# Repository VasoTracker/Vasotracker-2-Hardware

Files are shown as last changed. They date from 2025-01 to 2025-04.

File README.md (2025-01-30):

# VasoTracker 2.0

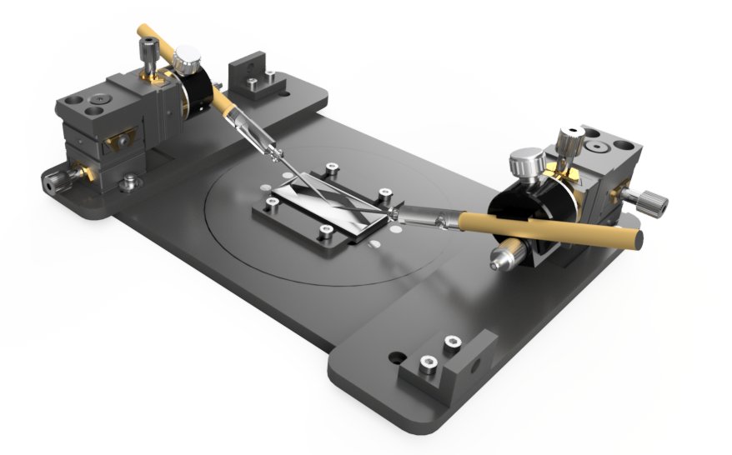
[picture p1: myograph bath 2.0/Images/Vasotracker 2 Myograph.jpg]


**VasoTracker 2.0** is a cost-effective, open-source system designed for measuring and tracking the diameter of isolated, pressurized blood vessels. As an accessible alternative to commercial pressure myograph systems, it costs approximately £13,500—about 25% of the price of typical commercial options.

Whether you’re new to vascular research or looking to optimize your lab's setup, VasoTracker 2.0 offers a modular and customizable solution for assessing blood vessel function.

For full details: see https://vasotracker.com/

## Table of Contents

- [Publications](#publications)
- [Core VasoTracker Components](#core-vasotracker-components)
- [Additional Components for a Complete System](#additional-components-for-a-complete-system)
- [Contributors for VasoTracker 2.0](#contributors-for-vasotracker-20)

## Publications

- VasoTracker 2.0 will soon be published as a preprint.
- The original VasoTracker 1.0 system is described here: DOI: [10.3389/fphys.2019.00099](https://www.frontiersin.org/articles/10.3389/fphys.2019.00099/full).
- [Click here to see a list of papers citing the first VasoTracker version](https://scholar.google.com/scholar?cites=12876987194916375307&as_sdt=2005&sciodt=0,5&hl=en).

## Core VasoTracker Components

**Approximate Build Cost: £3,320**

- **Bath Chamber (~£2,500)**  
  [Pressure Myograph](https://github.com/VasoTracker/VasoTracker-2/tree/main/myograph%20bath%202.0)
  
- **Temperature & Pressure Monitor (~£320)**  
  [Temperature & Pressure Sensor](https://github.com/VasoTracker/VasoTracker-2/tree/main/temperature%20%26%20pressure%20monitor)
  
- **VasoMoto Pressure Control System (~£500)**  
  [VasoMoto System](https://github.com/DrN8PhD/VasoMoto)
  
- **VasoTracker Software (Free)**  
  [VasoTracker Software](https://github.com/VasoTracker/VasoTracker-2/tree/main/vasotracker%202.0)

For details, refer to the [**VasoTracker 2.0 System Guide**](https://github.com/VasoTracker/VasoTracker-2/blob/main/VasoTracker%202%20System%20Guide.pdf).

## Additional Components for a Complete System

**Approximate Cost for New Components: £10,150**

To fully set up a VasoTracker-based pressure myography system, the following components are also required:

- **Microscope (inverted preferred) ~£5,000**
- **Camera (compatible with microscope) ~£400**
- **Laptop Computer (for data capture and analysis) ~£500**
- **Temperature Control System ~£4,250**

## Contributors for VasoTracker 2.0

**University of Strathclyde:**
- Calum Wilson
- Matthew D Lee
- John G McCarron
- Xun Zhang
- Charlotte Buckley

**University of Glasgow:**
- Christopher Osborne

**University of Vermont:**
- Osama Harraz

**Michigan State University:**
- Nathan R Tykocki

## License

Distributed under the terms of the [BSD-3-Clause] license,

VasoTracker is free and open source software/hardware.

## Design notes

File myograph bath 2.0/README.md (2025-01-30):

# VasoTracker 2.0 Pressure Myograph Chamber



The **VasoTracker 2.0 Pressure Myograph Chamber** is a multi-purpose design, and is ideal for experiments requiring blood vessel diameter measurement. The chamber was designed to sit on a standard microscope stage, but the baseplate was designed for compatibility with [Thorlabs motorized scanning stages](https://www.thorlabs.com/newgrouppage9.cfm?objectgroup_id=5360). Angled cannula holders allow vessels to be positioned near the coverglass at the bottom of the chamber for inverted confocal use, and also provide enough clearance to enable confocal imaging with large-diameter CFI60 on upright microscopes. 

We recommend that the custom parts are manufactured in POM-C material by commercial manufacturers (costs will scale with the number of baths ordered). 

## Table of Contents
- [Key Features](#key-Features)
- [Build & Operation Guide](#build--operation-guide)
- [Cost-Saving Tip](#cost-saving-tip)

## Key Features

- **Low-Volume Chamber:** The vessel chamber insert is designed for efficient use of reagents and environmental control, with only ~2 ml of volume.
- **Precision Positioning:** Independent XYZ positioning of both cannulas is enabled by dual pipette holders mounted on miniaturized 3-axis translation stages, ensuring accurate and flexible manipulation of vessels.
- **Precise Vessel Positioning:** The angled cannula design allows for easy vessel positioning near the coverslip, supporting low-working distance objectives on inverted microscopes, as well as water-dipping objectives on upright systems.
- **Durable Materials:** The base can be machined from POM-C, and the chamber insert from acrylic, making it durable and adaptable to various experimental conditions.
- **Magnetic Attachments:** Superfusion plumbing is attached securely with flexible magnetic holders, making it easy to manage and adjust.

## Build & Operation Guide

The monitor is constructed using readily available Arduino components. At the time of release, the total cost of the components is approximately **£315.66**, with pressure transducers accounting for a significant portion of the expense.

For a detailed list of components, step-by-step build instructions, and operational guidelines, please refer to the [**Bath Chamber User Manual**](https://github.com/VasoTracker/VasoTracker-2/blob/main/myograph%20bath%202.0/VasoTracker%202%20Bath%20Chamber%20Manual.pdf).

## Cost-Saving Tip

We recommend that the VasoTracker 2.0 Pressure Myograph  is machined out of POM-C (use acryllic for the actual chamber). Commercial CNC-machining costs scale with quantity - the price per unit drastically decreases when you order more than one of each part.

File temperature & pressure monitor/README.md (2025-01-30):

# VasoTracker Temperature & Pressure Monitor

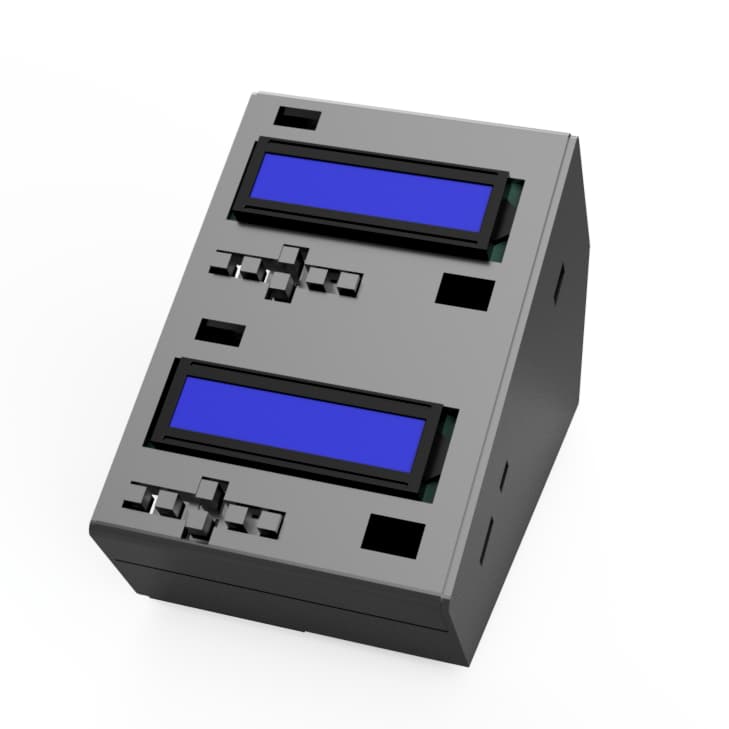
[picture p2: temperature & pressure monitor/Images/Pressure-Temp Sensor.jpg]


The **VasoTracker Temperature & Pressure Monitor** is an Arduino-based system designed for use with the VasoTracker myograph or any other setup that requires precise temperature and pressure monitoring. This modular device is easy to assemble and provides real-time data acquisition for experiments.

## Table of Contents
- [Key Features](#key-features-of-vasotracker-20)
- [Build & Operation Guide](#build--operation-guide)
- [Cost-Saving Tip](#cost-saving-tip)

## Key Features

- **Temperature Monitoring:** Accurately reads and displays temperature using a 10k NTC thermistor.
- **Pressure Monitoring:** Reads and displays pressure using flow-through pressure transducers.
- **Data Integration:** Streams data to the VasoTracker 2.0 GUI via the serial port for real-time acquisition and display.

## Build & Operation Guide

The monitor is constructed using readily available Arduino components. At the time of release, the total cost of the components is approximately **£315.66**, with pressure transducers accounting for a significant portion of the expense.

For a detailed list of components, step-by-step build instructions, and operational guidelines, please refer to the [**Temperature & Pressure Monitor User Manual**](https://github.com/VasoTracker/VasoTracker-2/blob/main/temperature%20%26%20pressure%20monitor/VasoTracker%202%20Temperature%20%26%20Pressure%20Monitor%20Manual.pdf).

## Cost-Saving Tip

You can significantly reduce the cost by opting for **disposable inline pressure transducers**, which are available for as low as **£10 each**. This is the approach used by VasoMoto to cut costs.

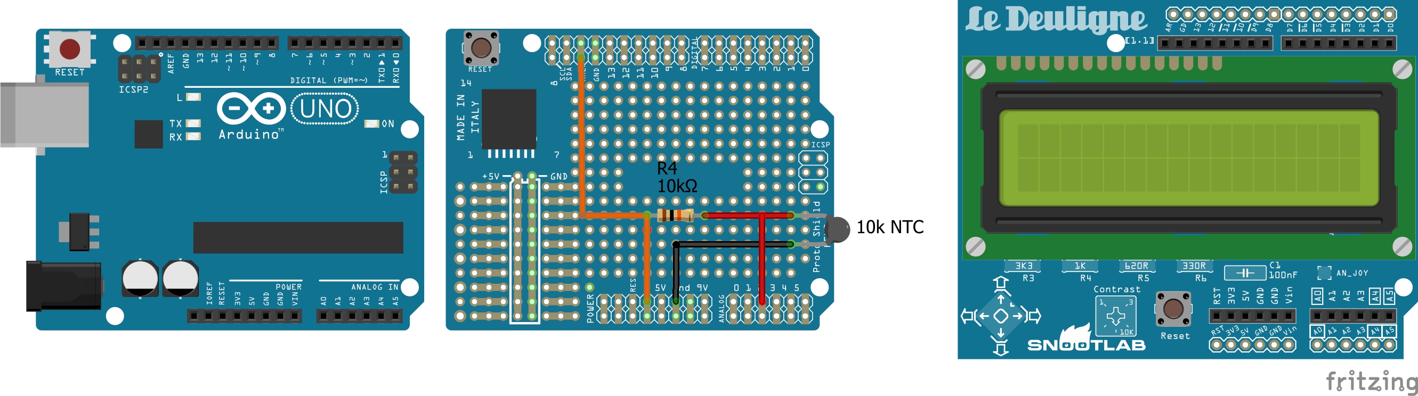
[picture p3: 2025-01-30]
temperature & pressure monitor/Images/Arduino Temp Sensor.jpg

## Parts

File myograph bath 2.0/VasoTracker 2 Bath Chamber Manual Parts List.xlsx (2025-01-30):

VasoTracker Pressure Myograph Chamber Parts
CNC Machined Components
Component | Supplier | Product # | Qty | Price | Total | Supplier Link
01_Nikon_Baseplate** | VasoTracker | - | 1 | £250.00 | £250.00 | VasoTracker GitHub (https://github.com/VasoTracker/VasoTracker-2/tree/main)
02_Chamber_Base** | VasoTracker | - | 1 | £130.00 | £130.00 | VasoTracker GitHub (https://github.com/VasoTracker/VasoTracker-2/tree/main)
03_Chamber_low_volume** | VasoTracker | - | 1 | £140.00 | £140.00 | VasoTracker GitHub (https://github.com/VasoTracker/VasoTracker-2/tree/main)
04_Clamp** | VasoTracker | - | 2 | £97.00 | £194.00 | VasoTracker GitHub (https://github.com/VasoTracker/VasoTracker-2/tree/main)
05_Tubing Connector** | VasoTracker | - | 2 | £99.00 | £198.00 | VasoTracker GitHub (https://github.com/VasoTracker/VasoTracker-2/tree/main)
**Prices scale with quantity!
Prices correct 10/2024 |  | Total |  |  | £912.00
3D Printed Components
Component | Supplier | Product # | Qty | Price | Total | Supplier Link
Magnetic Plumbing Holder | VasoTracker | - | 2 | £1.00 | £2.00 | VasoTracker GitHub (https://github.com/VasoTracker/VasoTracker-2/tree/main)
Prices correct 10/2024 |  | Total |  |  | £2.00
Commercial Components
Component | Supplier | Product # | Qty | Price | Total | Supplier Link
Micromanipulators | Thorlabs | DT12XYZ/M | 2 | £288.00 | £576.00 | Thorlabs (https://www.thorlabs.com/thorproduct.cfm?partnumber=DT12XYZ/m)
Rotatable cannula clamps | Siskiyou | MXC | 2 | £105.35 | £210.70 | Siskiyou (https://siskiyou.com/mxc/)
1.5 mm glass cannula holders | WPI Inc | MPH3 | 2 | £64.00 | £128.00 | WPI Inc (https://www.wpiinc.com/var-3819-microelectrode-holder-mph3.html)
Handle for cannula holder | WPI Inc | 2505 | 2 | £31.00 | £62.00 | WPI Inc (https://www.wpiinc.com/2505-electrode-handle-63-mm.html)
Perfusion plumbing (bend needles) | Needlez | NB16G1.5B90 | 2 | £0.68 | £1.36 | Needlez (https://www.needlez.co.uk/product/16g-blunt-needle-1-5inch-38mm-bent-tip-90-deg/)
Prices correct 10/2024 |  | Total |  |  | £978.06
Consumables & Miscellaneous Supplies
Component | Supplier | Product # | Qty | Price | Total | Supplier Link
Coverglass (50 mm by 24 mm) | MarienFeld | MARI0102222 | 1 | £107.00 | £107.00 | VWR (https://uk.vwr.com/store/product/7803457/cover-glasses-for-fluorescence)
50x Magnets | Amazon | 5 mm diameter, 1 mm thick | 1 | £5.59 | £5.59 | Amazon (https://www.amazon.co.uk/100PCS-Magnets-Neodymium-Whiteboards-Picture/dp/B09H2W3TQZ)
50x Magnets | Amazon | 5 mm diameter, 2 mm thick | 1 | £3.99 | £3.99 | Amazon (https://www.amazon.co.uk/FINDMAG-Neodymium-Magnets-Whiteboard-Hobbies/dp/B0C81GTN8P)
Superglue | Amazon | Gorilla Glue | 1 | £3.37 | £3.37 | Amazon (https://www.amazon.co.uk/Gorilla-Superglue-3g-Pack-2/dp/B001C5I4BO/)
M3 Socket Screws | Amazon | NB16G1.5B90 | 1 | £10.99 | £10.99 | Amazon (https://www.amazon.co.uk/gp/product/B09J2MNSMZ/)
M4 Socket Screws | Amazon | MARI0102222 | 1 | £10.99 | £10.99 | Amazon (https://www.amazon.co.uk/gp/product/B0CP1R19N5/)
Prices correct 10/2024 |  | Total |  |  | £141.93
Tubing & Connectors
Component | Supplier | Product # | Qty | Price | Total | Supplier Link
Masterflex 1.22 ID tubing (100 ft roll) | VWR | MFLX06449-31 | 1 | £201.00 | £201.00 | VWR (https://uk.vwr.com/store/item/EU7157222/masterflex-ismatec-microbore-pump-tubing-tygon-s3tm-e-lfl-avantor)
Masterflex 1.52 ID tubing (100 ft roll) | VWR | MFLX06460-36 | 1 | £157.00 | £157.00 | VWR (https://uk.vwr.com/store/item/EU7098238/masterflex-ismatec-microbore-pump-tubing-tygon-e-lab-avantor)
Female luer (1/16" barb; pack of 25) | VWR | GY-45502-00 | 1 | £28.90 | £28.90 | VWR (https://uk.vwr.com/store/item/EU7104706/masterflex-adapter-fittings-female-luer-to-hose-barb-bulkhead-polypropylene-avantor)
Male luer (1/16" barb; pack of 25) | VWR | MFLX45504-00 | 1 | £20.40 | £20.40 | VWR (https://uk.vwr.com/store/item/EU7104664/masterflex-adapter-fittings-male-luer-to-hose-barb-straight-polycarbonate-avantor)
Luer stopcock (pack of 10) | VWR | MFLX30600-02 | 1 | £34.60 | £34.60 | VWR (https://uk.vwr.com/store/item/EU7103411/masterflex-luer-stopcock-fittings-polycarbonate-avantor)
Threaded Luer (pack of 25) | VWR | MFLX45508-30 | 1 | £28.90 | £28.90 | VWR (https://uk.vwr.com/store/item/EU7104706/masterflex-adapter-fittings-female-luer-to-hose-barb-bulkhead-polypropylene-avantor)
Prices correct 10/2024 |  | Total |  |  | £470.80
Total Price |  |  |  |  | £2504.79

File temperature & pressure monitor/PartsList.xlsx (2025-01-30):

VasoTracker Temperature & Pressure Monitor Parts
3D Printed Parts
3D Printed Enclosure | VasoTracker | - | 1 | £0 | £0 | GitHub (https://github.com/VasoTracker/VasoTracker-2)
Prices correct 10/2024 |  | Total |  |  | £0.00
VasoTracker Temperature Monitor
Component | Supplier | Product # | Qty | Price | Total | Supplier Link
Arduino Uno** | Arduino | RB-Ard-34 | 1 | £26.50 | £26.50 | RobotShop (https://uk.robotshop.com/products/arduino-uno-r3-usb-microcontroller)
12V power supply | RS | 903-7048 | 1 | £8.33 | £8.33 | RS (https://uk.rs-online.com/web/p/ac-dc-adapters/1753303)
Arduino Proto Shield | Skinflint | A000077 | 1 | £13.50 | £13.50 | SkinFlint (https://skinflint.co.uk/arduino-proto-shield-uno-a000077-a799462.html)
LCD Shield | RobotShop | RB-Cyt-73 | 1 | £3.64 | £3.64 | RobotShop (https://uk.robotshop.com/products/cytron-lcd-keypad-shield-arduino)
10k NTC Thermistor | Adafruit | 372 | 1 | £3.06 | £3.06 | DigiKey (https://www.digikey.co.uk/en/products/detail/adafruit-industries-llc/372/6051772)
Resistor kit | RobotShop | RES-E12 | 1 | £13.80 | £13.80 | RobotShop (https://uk.robotshop.com/products/resistor-kit-610pk)
Jumper wire kit | RobotShop | RB-Cix-02 | 1 | £3.77 | £3.77 | RobotShop (https://uk.robotshop.com/products/140-piece-pre-formed-jumper-wire-kit)
2-pin Screw Terminal | RobotShop | RB-Dfr-465 | 1 | £0.76 | £0.76 | RobotShop (https://uk.robotshop.com/products/2-pin-screw-terminal-35mm)
Prices correct 10/2024 |  | Total |  |  | £73.36
VasoTracker Pressure Monitor
Component | Supplier | Product # | Qty | Price | Total | Supplier Link
Arduino Uno** | Arduino | RB-Ard-34 | 1 | £26.50 | £26.50 | RobotShop (https://uk.robotshop.com/products/arduino-uno-r3-usb-microcontroller)
12V power supply | RS | 903-7048 | 1 | £8.33 | £8.33 | RS (https://uk.rs-online.com/web/p/ac-dc-adapters/1753303)
Wheatstone bridge amplifier shield | RobotShop | RB-Onl-38 | 1 | £45.63 | £45.63 | RobotShop (https://www.robotshop.com/uk/strain-gauge-load-cell-amplifier-shield-2ch.html)
LCD Shield | RobotShop | RB-Cyt-73 | 1 | £3.64 | £3.64 | RobotShop (https://uk.robotshop.com/products/cytron-lcd-keypad-shield-arduino)
Inline pressure transducers | Honeywell | 26PCDFG5G | 2 | £74.55 | £149.10 | Mouser (https://www.mouser.co.uk/ProductDetail/Honeywell/26PCDFG5G/)
12” 4-pin jumper wire | RobotShop | RB-Spa-1107 | 2 | £0.60 | £1.20 | RobotShop (https://uk.robotshop.com/products/12-4-pin-jumper-wire)
Arduino stackable headers | RobotShop | RB-Spa-928 | 1 | £1.67 | £1.67 | RobotShop (https://uk.robotshop.com/products/arduino-r3-stackable-headers)
Female to female jumper | RobotShop | RB-Gog-65 | 1 | £4.31 | £4.31 | RobotShop (https://uk.robotshop.com/products/assorted-silicon-wire-jumper-22-awg-65pk-f-f)
Heatshrink tubing | RobotShop | RB-Gog-47 | 1 | £1.92 | £1.92 | RobotShop (https://uk.robotshop.com/products/shrink-tube-variety-pack)
Prices correct 10/2024 |  | Total |  |  | £242.30
Total Price |  |  |  |  | £315.66

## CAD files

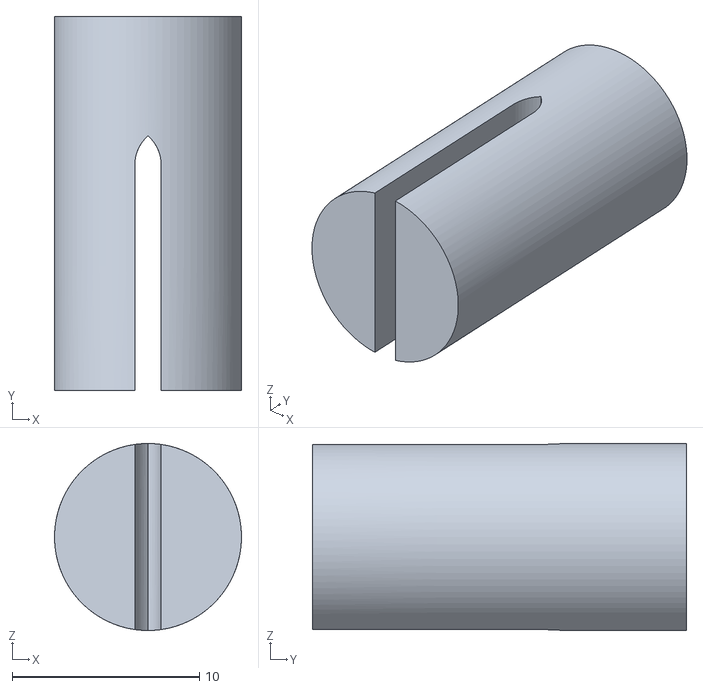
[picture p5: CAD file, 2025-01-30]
myograph bath 2.0/3D Print Files/plumbing_holder_large v1.stl
10.0 x 20.0 x 10.0

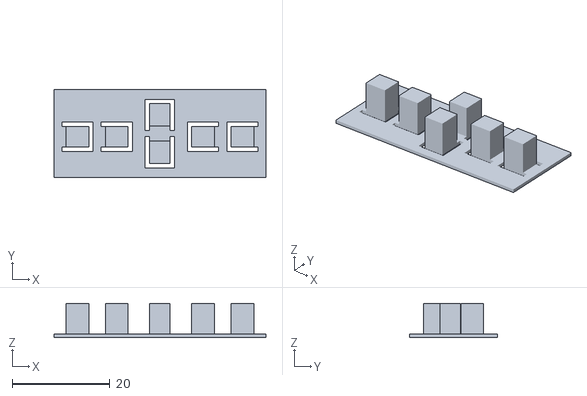
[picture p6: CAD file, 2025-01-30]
temperature & pressure monitor/3D Printed Enclosures/CombiBox/buttons.stl
43.3 x 18.0 x 7.02

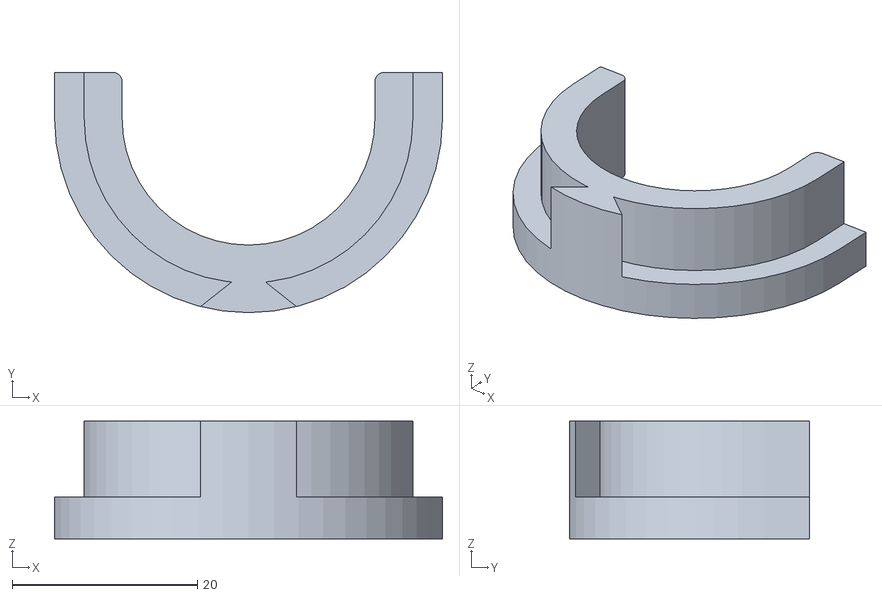
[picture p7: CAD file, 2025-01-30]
temperature & pressure monitor/3D Printed Enclosures/VasoMoto/VasoMoto Printed Parts/VasoMoto-tubing-spacer-2.stl
41.9 x 26.0 x 12.7

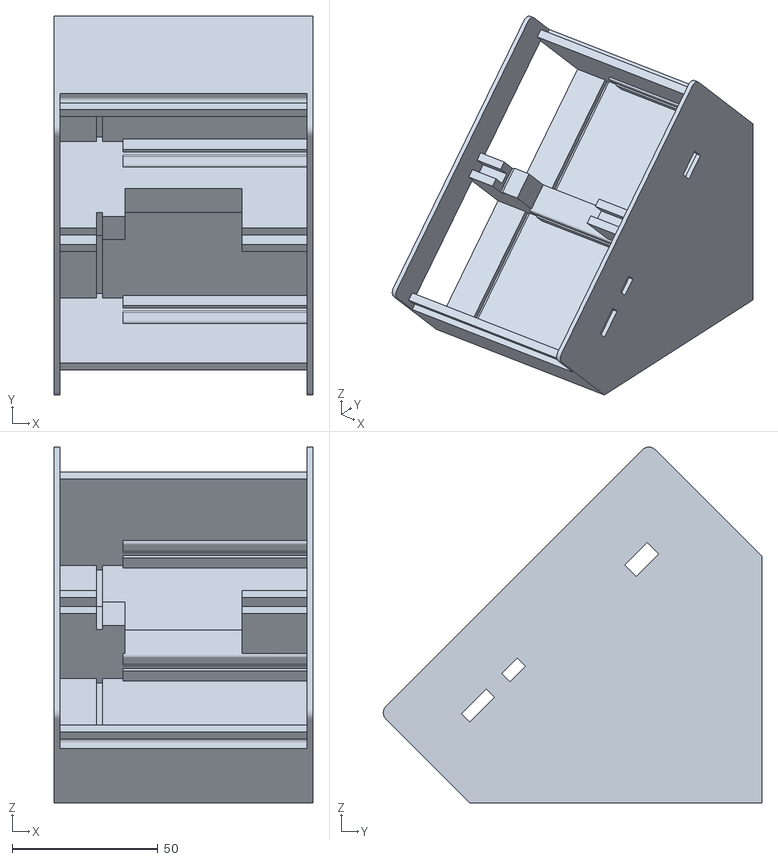
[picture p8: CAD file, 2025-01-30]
temperature & pressure monitor/3D Printed Enclosures/CombiBox/Arduino V7 combibox base.stl
88.6 x 129.8 x 122.0

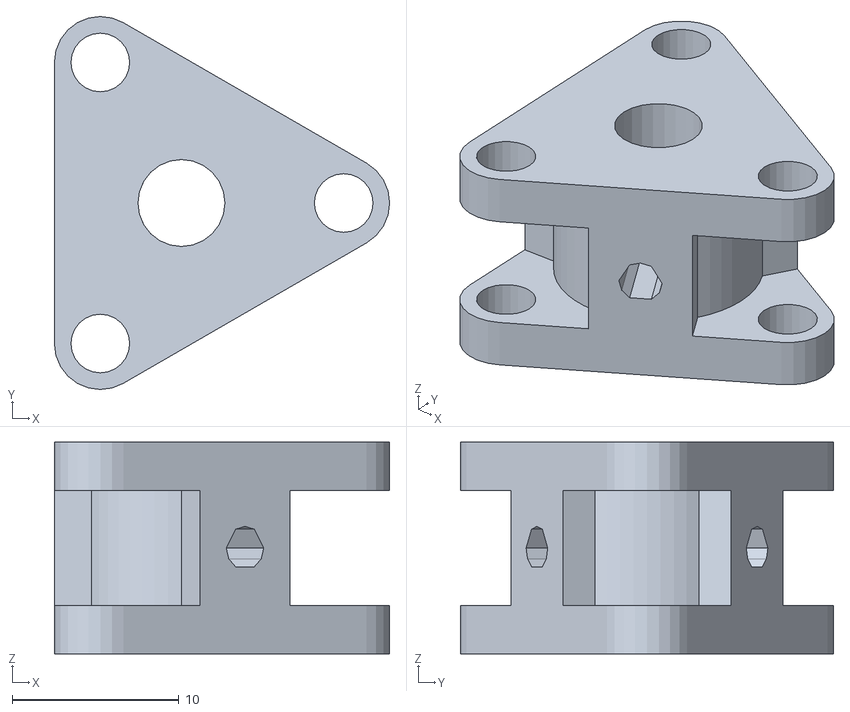
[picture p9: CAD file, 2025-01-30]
temperature & pressure monitor/3D Printed Enclosures/VasoMoto/VasoMoto Printed Parts/VasoMoto-pumphead.stl
20.1 x 22.4 x 12.7

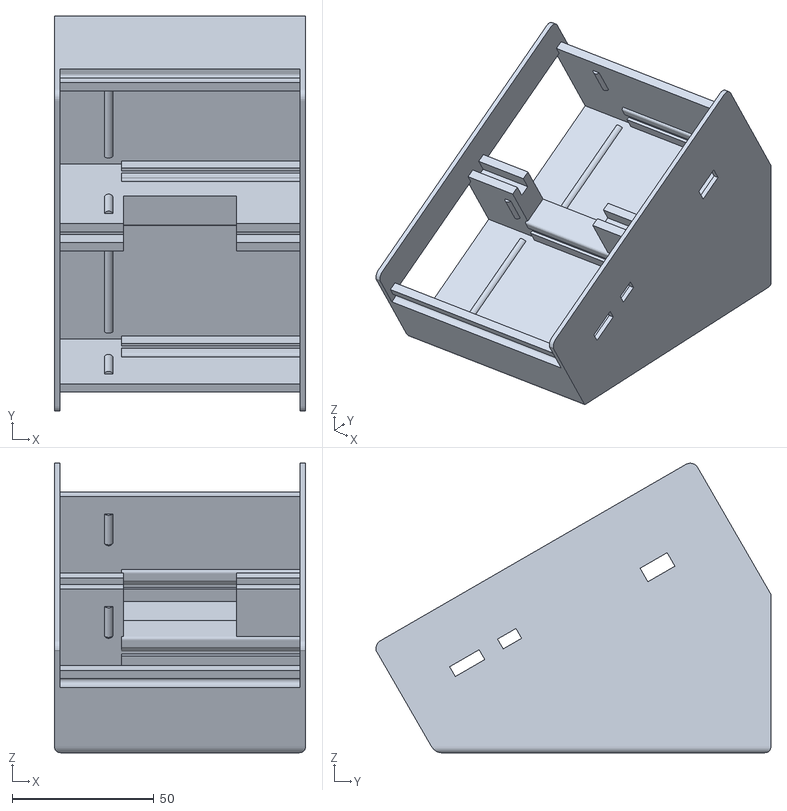
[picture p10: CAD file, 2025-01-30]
temperature & pressure monitor/3D Printed Enclosures/CombiBox/Arduino V7 combibox base 2.stl
88.6 x 139.3 x 102.2

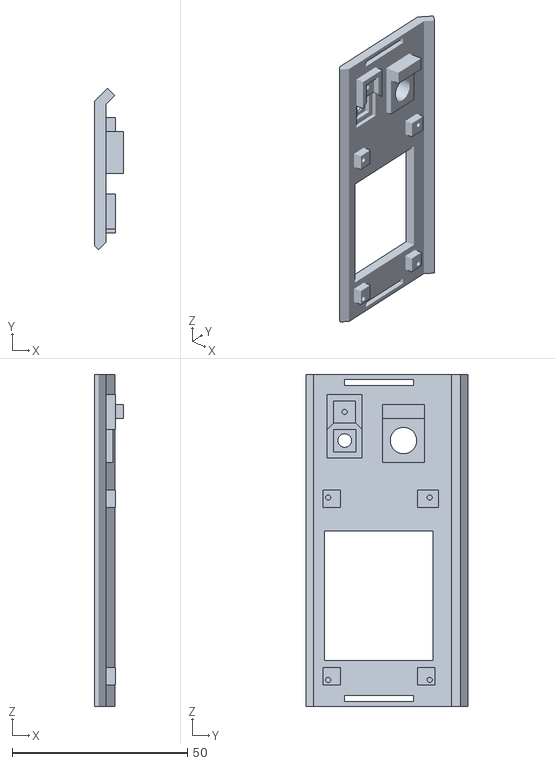
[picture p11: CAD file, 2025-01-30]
temperature & pressure monitor/3D Printed Enclosures/VasoMoto/VasoMoto Printed Parts/VasoMoto-LCD-button.stl
8.29 x 46.2 x 94.8

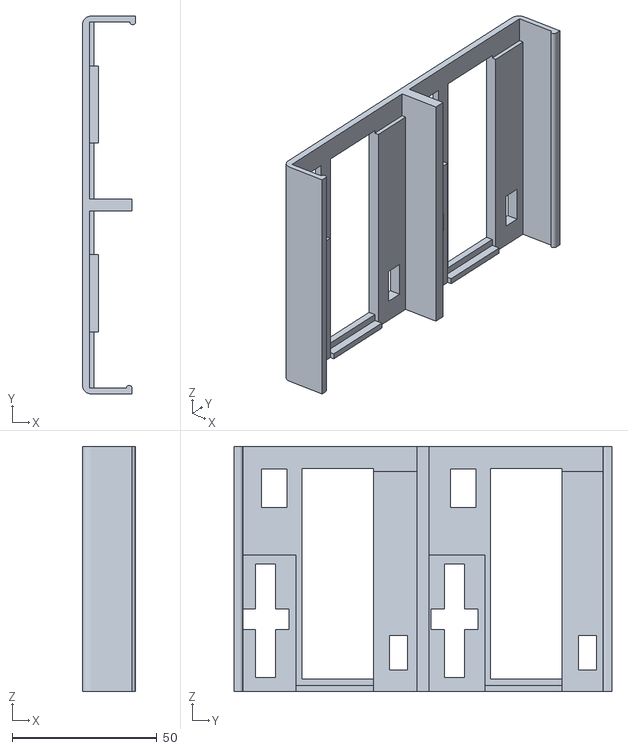
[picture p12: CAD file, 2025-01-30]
temperature & pressure monitor/3D Printed Enclosures/CombiBox/Arduino V7 combibox lid.stl
18.4 x 130.5 x 84.6

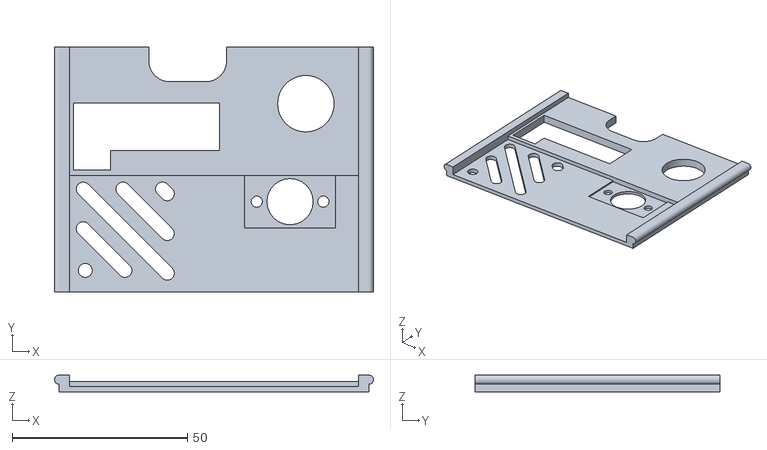
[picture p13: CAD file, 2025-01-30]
temperature & pressure monitor/3D Printed Enclosures/VasoMoto/VasoMoto Printed Parts/VasoMoto-back.stl
91.0 x 70.0 x 4.80

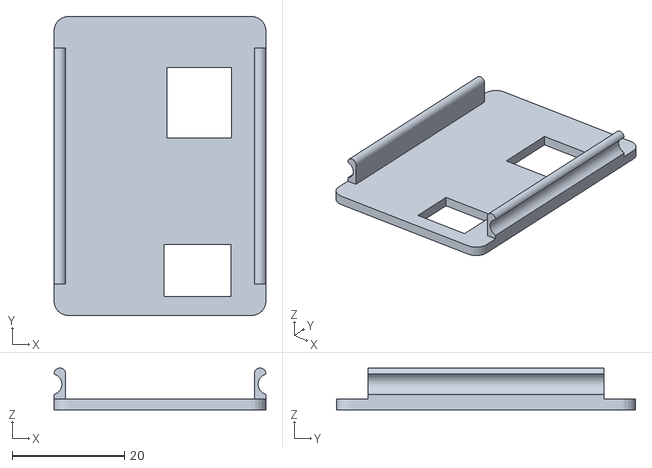
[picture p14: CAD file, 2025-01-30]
temperature & pressure monitor/3D Printed Enclosures/CombiBox/Arduino V7 combibox side.stl
37.7 x 53.2 x 7.45

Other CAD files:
temperature & pressure monitor/3D Printed Enclosures/Pressure Monitor Case/Step/Case_V5_Pressure_LCD_buttons v1.step
temperature & pressure monitor/3D Printed Enclosures/Temperature Monitor Case/Step/Case_V6_Temp_LCD_Case v1.step
temperature & pressure monitor/3D Printed Enclosures/Pressure Monitor Case/Step/Case_V5_Pressure_LCD_txdx_lid v1.step
temperature & pressure monitor/3D Printed Enclosures/Temperature Monitor Case/Step/Case_V6_Temp_LCD_cover_pwr v1.step
temperature & pressure monitor/3D Printed Enclosures/Pressure Monitor Case/Step/Case_V5_Pressure_LCD_cover v1.step
temperature & pressure monitor/3D Printed Enclosures/Temperature Monitor Case/Step/Case_V6_Temp_LCD_cover v1.step
temperature & pressure monitor/3D Printed Enclosures/Pressure Monitor Case/Step/Case_V5_Pressure_LCD_Component#7 v1.step
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

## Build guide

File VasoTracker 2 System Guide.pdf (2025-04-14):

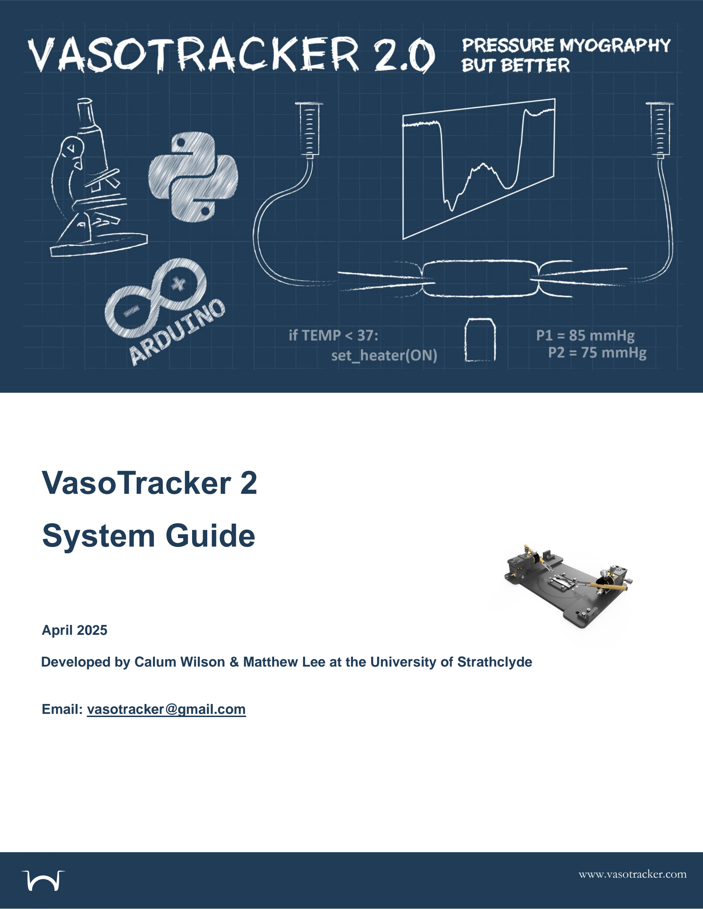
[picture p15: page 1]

# VasoTracker 2

# System Guide

April 2025

Developed by Calum Wilson & Matthew Lee at the University of Strathclyde

Email: vasotracker@gmail.com

www.vasotracker.com

TABLE OF CONTENTS | PAGE | 1

## Table of Contents

Affordable, Open-Source Pressure Myography Core VasoTracker Components
Citing VasoTracker

Inexpensive Microscope Options New Microscope Recommendations

Inexpensive Camera Options
New Camera Recommendations

Recommended Desktop Specifications Recommended Laptop Specifications

Temperature Monitoring
Temperature Control
Solution Control

Pressure Monitoring
Pressure Regulation Options

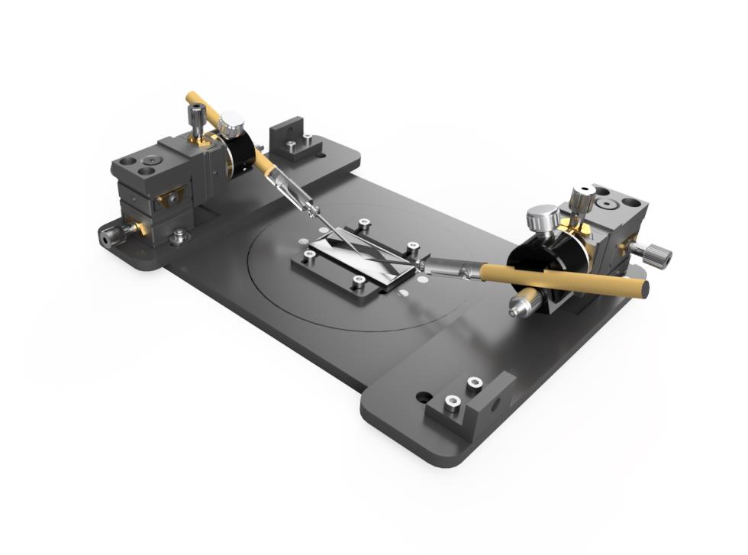
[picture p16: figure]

OVERVIEW | PAGE | 2

## Overview

OVERVIEW | PAGE | 3

Affordable, Open-Source Pressure Myography

VasoTracker 2.0 is a cost-effective, open-source system designed to measure and track the diameter of isolated, pressurized blood vessels. This accessible alternative to commercial pressure myograph systems costs approximately £13,500, roughly 25% of the cost of commercial options.

Whether you’re new to vascular research or seeking to optimize your lab's setup, VasoTracker 2.0 provides a modular and customizable solution. This guide provides an overview of core and additional components, alongside recommendations, to help you create a complete pressure myography system.

Core VasoTracker Components

Approximate build cost: £3320

- Bath Chamber (~£2,500)
- https://vasotracker.com/pressure-myograph/
- Temperature & Pressure Monitor (~£320)
- https://vasotracker.com/temperature-pressure-sensor/
- VasoMoto Pressure Control System (~£500)
- https://vasotracker.com/vasomoto/
- VasoTracker Software (free)
- https://vasotracker.com/software/

Additional Components for a Complete System (approximate cost for new components: £10,150)

To fully set up a VasoTracker-based pressure myography system, the following are also required. Approximate cost for new compponents: £10,150.

- Microscope (inverted preferred, ~£5000)
- Camera (compatible with microscope, ~£400)
- Laptop Computer (for data capture and analysis, ~£500)
- Temperature control system (~£4250)

For more information on building your own VasoTracker system, visit https://vasotracker.com/.

Citing VasoTracker

For citation details, please visit: https://vasotracker.com/publications/

RECOMMENDED MICROSCOPES | PAGE | 4

## Recommended Microscopes

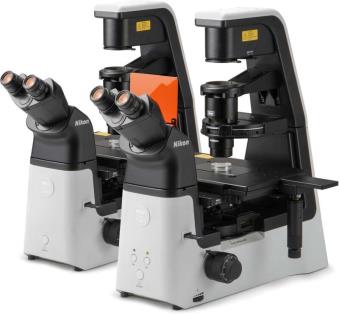
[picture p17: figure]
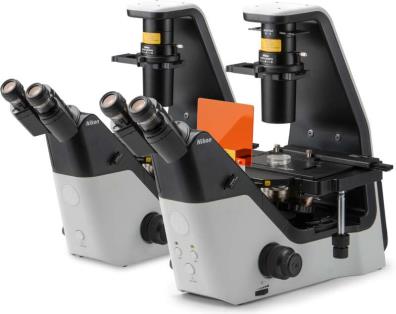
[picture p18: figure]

RECOMMENDED MICROSCOPES | PAGE | 5

The VasoTracker pressure myography chamber offers flexibility for researchers, being compatible with both inverted and upright microscopes. We suggest an inverted trinocular microscope with a camera port for optimal use.

Inexpensive Microscope Options

Most microscopes will work, and many researchers will be able to find a suitable microscope lying around in their department. A good source of inexpensive second-hand microscopes is eBay (we have purchased Olympus CK40 and CKX41 microscopes for less than £1000 each).

New Microscope Recommendations

At Strathclyde, we like Nikon microscopes, so here are two models that fit different budgets:

### 1. Nikon Ts2R (Price ~ £8,000)

- Requirements:
- Camera port & c-mount adapter
- Objectives (4x, 10x, 20x, 40x).
- Benefits:
- This microscope has a very nice mechanical stage.
- Nice optics.
- Can be configured in any way you want (fluorescence options)

https://www.microscope.healthcare.nikon.com/products/inverted-microscopes/eclipse-ts2r

### 2. Nikon Ts2 (Price ~ £4,000)

- Requirements:
- Camera port & c-mount adapter
- Objectives (4x, 10x, 20x, 40x).
- Benefits:
- Cheap
- Nice optics
- Drawbacks:
- The stage! We remove it, and just sit the myograph on directly on the microscope. This is a pain if you want fine control of where the artery is.

https://www.microscope.healthcare.nikon.com/products/inverted-microscopes/eclipse-ts2

RECOMMENDED CAMERAS | PAGE | 6

## Recommended Cameras

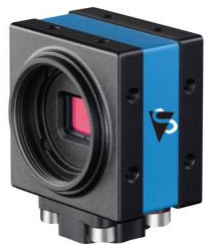
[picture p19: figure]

RECOMMENDED CAMERAS | PAGE | 7

The VasoTracker pressure myography software is powered by Python 3 and µManager 2.0. This combination facilitates lots of different camera compatibility.

Inexpensive Camera Options

If a camera works in uManager 2.0, then you should be able to get it to work with VasoTracker. So any cheap camera that works with OpenCV should work.

New Camera Recommendations

We have fully tested and regularly use the following cameras:

### 1. Thorlabs CS165MU/M (Price ~ £400)

- Requirements:
- Camera (~£380)
- C-mount adapter (~£18)

Camera: https://www.thorlabs.com/thorproduct.cfm?partnumber=CS165MU/M C-mount adapter: https://www.thorlabs.com/thorproduct.cfm?partnumber=SM1A10 (https://eur02.safelinks.protection.outlook.com/?reserved=0)

### 2. Basler Ace 2 (a2A1920-160um)

- Requirements:
- Camera (~£380)
- USB 3.0 Cable (~£6)

Camera: https://www.baslerweb.com/en/shop/a2a1920-160umbas USB 3.0 Cable: https://www.amazon.co.uk/dp/B0CQCNTLZM/

### 3. The Imaging Source (DMK 42AUC03, Monochrome)

- Requirements:
- Camera (~£200)
- USB 3.0 Cable (~£6)

Camera: https://www.theimagingsource.com/en-us/product/industrial/2u/dmk42auc03/ USB 3.0 Cable: https://www.amazon.co.uk/dp/B0CQCNTLZM/

RECOMMENDED COMPUTERS | PAGE | 8

## Recommended Computers

RECOMMENDED COMPUTERS | PAGE | 9

For optimal performance when running the VasoTracker system, we recommend a desktop or laptop with the following specifications:

Recommended Desktop Specifications

- Operating System: Windows 10 or newer
- Memory (RAM): 16 GB minimum
- Storage: SSD (Solid State Drive) for efficient data handling
- Processor: Intel i5 or higher for robust performance

An HP desktop with these specifications generally costs around £700. Desktop setups can be particularly advantageous in lab environments, offering reliable integration with peripherals and long-term stability for intensive data processing.

Example desktop computer:

HP Pro Mini 400 G9 Business Desktop - Core™ i5

- Link: https://www.hp.com/gb-en/shop/product.aspx?id=997S0ET&opt=ABU&sel=DTP
- Cost: £710

Recommended Laptop Specifications

- Operating System: Windows 10 or newer
- Memory (RAM): 16 GB minimum for smooth data processing and analysis
- Storage: SSD (Solid State Drive) to ensure faster boot times and efficient data handling
- Processor: Intel i5 or higher for adequate processing power

A HP laptop with these specifications typically costs around £1000+. We really do recommend a desktop option though.

Example laptop computer:

HP EliteBook 840 G11 14” Business Laptop – Core™ Ultra 7

- Link: https://www.hp.com/gb-en/shop/product.aspx?id=8A4U3EA&opt=ABU&sel=NTB&_gl=1
- Cost: £1320

TEMPERATURE CONTROL OPTIONS | PAGE | 10

## Temperature Control Options

TEMPERATURE CONTROL OPTIONS | PAGE | 11

Temperature Monitoring

The VasoTracker Temperature & Pressure Monitor provides real-time temperature monitoring within the bath chamber. A sensor placed in the bath chamber connects to VasoTracker 2.0 software, offering continuous temperature data for precise control. The device can be built for ~£320.

Full build details here: https://vasotracker.com/temperature-pressure-sensor/

Temperature Control

To regulate temperature, VasoTracker 2.0 relies on external temperature control systems. Here are some recommended setups with estimated costs as of October 2024:

### 1. Hotplate Stirrer & Peristaltic Pump (~£3500):

- Hotplate Stirrer (https://uk.vwr.com/store/catalog/product.jsp?catalog_number=442-1274) (~£500)
- 2-channel Masterflex Ismatec Reglo Peristaltic Pump (https://uk.vwr.com/store/product/38705714/masterflex-ismatec-reglo-independent-channel-control-icc-peristaltic-pumps-avantor) (~£3000)

### 2. Heated Circulator & Peristaltic Pump (~£4250)

- Optima T100 Heated Circulating Bath (https://www.fishersci.co.uk/shop/products/digital-heated-circulating-baths-10/12757809) (~£1000)
- Radnoti Heating Coil (1.5 mL) (https://www.adinstruments.com/products/radnoti-heating-coils#158823) (~£250)
- 2-channel Masterflex Ismatec Reglo Peristaltic Pump (https://uk.vwr.com/store/product/38705714/masterflex-ismatec-reglo-independent-channel-control-icc-peristaltic-pumps-avantor) (~£3000)

### 3. Inline Solution Heater & Peristaltic Pump (~£5500)

- Warner SH-27B inline solution heater & TC-324C Controller (https://www.warneronline.com/single-inline-solution-heaters-sh-27b-sf-28) (~£2500)
- 2-channel Masterflex Ismatec Reglo Peristaltic Pump (https://uk.vwr.com/store/product/38705714/masterflex-ismatec-reglo-independent-channel-control-icc-peristaltic-pumps-avantor) (~£3000)
•

Solution Control

To maintain a constant solution volume in the bath, it is recommended to use a 2-channel peristaltic pump.

Adjusting the Bath Volume:
- The VasoTracker 2.0 chamber offers two bath configurations:
- Low-volume chamber: 2 mL capacity
- Higher-volume chamber: 3.5 mL capacity
- Adjust bath volume by raising or lowering the perfusion plumbing.

Tip: Using larger tubing on the outflow side helps prevent overflow if both channels of the peristaltic pump are set to the same speed.

PRESSURE CONTROL OPTIONS | PAGE | 12

## Pressure Control Options

PRESSURE CONTROL OPTIONS | PAGE | 13

Pressure Monitoring

The VasoTracker Temperature & Pressure Monitor provides real-time pressure monitoring via two inline pressure transducers connected to the VasoTracker bath chamber. The device continuously streams pressure data to the VasoTracker software. The device can be built for ~£320.

Full build details here: https://vasotracker.com/temperature-pressure-sensor/

Pressure Regulation Options

VasoTracker 2.0 supports two main types of pressure regulation systems (estimated costs as of October 2024):

Hydrostatic Gravity Columns (for experiments requiring flow through the blood vessel lumen)

### 1. Gravity-driven perfusion system (cost ~£400):

- Setup: 50 ml syringes mounted on magnetic holders connected to each side of the pressure myograph.
- Operation:
- Maintain constant pressure without flow by setting syringes at equal height.
- Adjust pressure by raising or lowering the syringe height.
- Introduce flow without changing pressure by moving syringes up/down in opposite directions.
- Monitoring: Pressure can be observed using the VasoTracker Pressure Monitor.

Pressure Servo Controllers (for no-flow experiments, e.g. assessing myogenic tone)

### 1. VasoMoto Open-source Pressure Servo Controller (cost ~£200):

- Features: Integrates directly with VasoTracker via USB, allowing VasoTracker software to control it (does not require the VasoTracker Pressure Monitor).
- Full build details here: https://vasotracker.com/vasomoto/

### 2. Commercial Pressure Servo Controller Systems (e.g., Living Systems LS-PS-200. ~£4000):

- VasoTracker software can control the LS-PS-200 via the following peripherals (full instructions can be found in the VasoTracker software manual):
- National Instruments DAQ Board (e.g. USB-6001, (https://www.ni.com/en-gb/shop/model/usb-6001.html) ~£275).
- A BNC cable (e.g. Amphenol 115101-35-M1.00, (https://www.mouser.co.uk/ProductDetail/Amphenol-RF/115101-35-M1.00?qs=7bTaA%2FLYtSZR6yx2j%2FaqjQ%3D%3D) ~£25)
- A BNC breakout cable (e.g. Pomona 4969, (https://www.mouser.co.uk/ProductDetail/Pomona-Electronics/4969) ~£15)

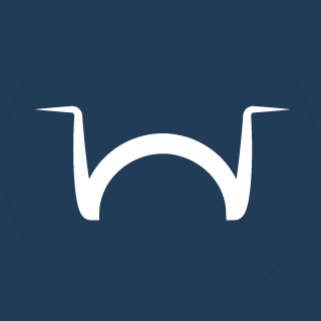
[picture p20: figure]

www.vasotracker.com

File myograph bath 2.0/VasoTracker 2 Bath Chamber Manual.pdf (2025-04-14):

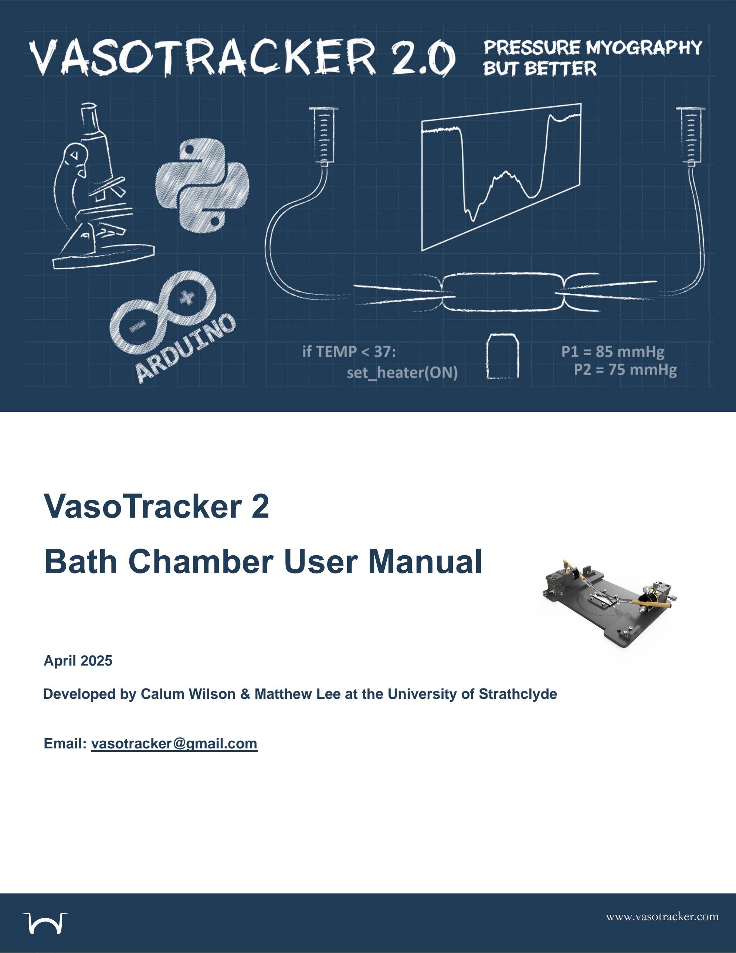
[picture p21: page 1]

# VasoTracker 2

# Bath Chamber User Manual

April 2025

Developed by Calum Wilson & Matthew Lee at the University of Strathclyde

Email: vasotracker@gmail.com

www.vasotracker.com

TABLE OF CONTENTS | PAGE | 1

## Table of Contents

The VasoTracker 2.0 Pressure Myograph Bath Chamber
Key Features
Citing VasoTracker
Parts List

Step by Step Guide
Replacing the Glass Cannula

Mounting the Vessel onto the Cannula Pressurizing the Vessel
Checking the viability of the blood vessel


OVERVIEW | PAGE | 2

## Overview

OVERVIEW | PAGE | 3

The VasoTracker 2.0 Pressure Myograph Bath Chamber

The VasoTracker 2.0 Pressure Myograph Bath Chamber is an open-source, low-cost imaging chamber for pressure myography experiments. The chamber consists of a durable base and a low-volume (~2 ml) vessel chamber insert, optimized for efficient reagent use and precise environmental control through superfusion.

Key Features

- Low-Volume Chamber: The vessel chamber insert is designed for efficient use of reagents and environmental control, with only ~2 ml of volume.
- Precision Positioning: Independent XYZ positioning of both cannulas is enabled by dual pipette holders mounted on miniaturized 3-axis translation stages, ensuring accurate and flexible manipulation of vessels.
- Precise Vessel Positioning: The angled cannula design allows for easy vessel positioning near the coverslip, supporting low-working distance objectives on inverted microscopes, as well as water-dipping objectives on upright systems.
- Durable Materials: The base can be machined from POM-C, and the chamber insert from acrylic, making it durable and adaptable to various experimental conditions.
- Magnetic Attachments: Superfusion plumbing is attached securely with flexible magnetic holders, making it easy to manage and adjust.

Citing VasoTracker

VasoTracker began life with the support of the Wellcome Trust and the British Heart Foundation to facilitate research on blood vessel function. Our ability to continue supporting, developing, and maintaining VasoTracker depends on further grant funding. If you use VasoTracker in any way, please cite VasoTracker in your scientific publications. For citation details, please visit: https://vasotracker.com/publications/

OVERVIEW | PAGE | 4

Parts List

VasoTracker Pressure Myograph Chamber Parts

CNC Machined Components | Supplier | Product # | Qty | Price | Total | Supplier Link
01_Nikon_Baseplate** | VasoTracker | - | 1 | £250.00 | £250.00 | VasoTracker
| | | | | | GitHub (https://github.com/VasoTracker/VasoTracker-2/tree/main)
02_Chamber_Base** | VasoTracker | - | 1 | £130.00 | £130.00 | VasoTracker
| | | | | | GitHub (https://github.com/VasoTracker/VasoTracker-2/tree/main)
03_Chamber_low_volume** | VasoTracker | - | 1 | £140.00 | £140.00 | VasoTracker
| | | | | | GitHub (https://github.com/VasoTracker/VasoTracker-2/tree/main)
04_Clamp** | VasoTracker | - | 2 | £97.00 | £194.00 | VasoTracker
| | | | | | GitHub (https://github.com/VasoTracker/VasoTracker-2/tree/main)
05_Tubing Connector** | VasoTracker | - | 2 | £99.00 | £198.00 | VasoTracker
| | | | | | GitHub (https://github.com/VasoTracker/VasoTracker-2/tree/main)
**Prices scale with quantity!
Prices correct 10/2024 | | Total | | | £912.00
3D Printed Components | Supplier | Product # | Qty | Price | Total | Supplier Link
Magnetic Plumbing Holder | VasoTracker | - | 2 | £1.00 | £2.00 | VasoTracker GitHub (https://github.com/VasoTracker/VasoTracker-2/tree/main)
Prices correct 10/2024 | | Total | | | £2.00
Commercial Components | Supplier | Product # | Qty | Price | Total | Supplier Link
Micromanipulators | Thorlabs | DT12XYZ/M | 2 | £288.00 | £576.00 | Thorlabs (https://www.thorlabs.com/thorproduct.cfm?partnumber=DT12XYZ/m)
Rotatable cannula clamps | Siskiyou | MXC | 2 | £105.35 | £210.70 | Siskiyou (https://siskiyou.com/mxc/)
1.5 mm glass cannula holders | WPI Inc | MPH3 | 2 | £64.00 | £128.00 | WPI Inc (https://www.wpiinc.com/var-3819-microelectrode-holder-mph3.html)
Handle for cannula holder | WPI Inc | 2505 | 2 | £31.00 | £62.00 | WPI Inc (https://www.wpiinc.com/2505-electrode-handle-63-mm.html)
Perfusion plumbing | Needlez | NB16G1.5B90 | 2 | £0.68 | £1.36 | Needlez (https://www.needlez.co.uk/product/16g-blunt-needle-1-5inch-38mm-bent-tip-90-deg/)
Prices correct 10/2024 | | Total | | | £978.06
Consumables & Miscellaneous Supplies | Supplier | Product # | Qty | Price | Total | Supplier Link
Coverglass (50 mm by 24 mm) | MarienFeld | MARI0102222 | 1 | £107.00 | £107.00 | VWR (https://uk.vwr.com/store/product/7803457/cover-glasses-for-fluorescence)
50x Magnets | Amazon | 5 mm ⌀ x 1 mm | 1 | £5.59 | £5.59 | Amazon (https://www.amazon.co.uk/100PCS-Magnets-Neodymium-Whiteboards-Picture/dp/B09H2W3TQZ)
50x Magnets | Amazon | 5 mm ⌀ x 2 mm | 1 | £3.99 | £3.99 | Amazon (https://www.amazon.co.uk/FINDMAG-Neodymium-Magnets-Whiteboard-Hobbies/dp/B0C81GTN8P)
Superglue | Amazon | Gorilla Glue | 1 | £3.37 | £3.37 | Amazon (https://www.amazon.co.uk/Gorilla-Superglue-3g-Pack-2/dp/B001C5I4BO/)
M3 Socket Screws | Amazon | NB16G1.5B90 | 1 | £10.99 | £10.99 | Amazon (https://www.amazon.co.uk/gp/product/B09J2MNSMZ/)
M4 Socket Screws | Amazon | MARI0102222 | 1 | £10.99 | £10.99 | Amazon (https://www.amazon.co.uk/gp/product/B0CP1R19N5/)
Prices correct 10/2024 | | Total | | | £141.93
Tubing & Connectors | Supplier | Product # | Qty | Price | Total | Supplier Link
Masterflex 1.22 ID tubing (100 ft) | VWR | MFLX06449-31 | 1 | £201.00 | £201.00 | VWR (https://uk.vwr.com/store/item/EU7157222/masterflex-ismatec-microbore-pump-tubing-tygon-s3tm-e-lfl-avantor)
Masterflex 1.52 ID tubing (100 ft) | VWR | MFLX06460-36 | 1 | £157.00 | £157.00 | VWR (https://uk.vwr.com/store/item/EU7098238/masterflex-ismatec-microbore-pump-tubing-tygon-e-lab-avantor)
Female luer (1/16" barb; pack of 25) | VWR | GY-45502-00 | 1 | £28.90 | £28.90 | VWR (https://uk.vwr.com/store/item/EU7104706/masterflex-adapter-fittings-female-luer-to-hose-barb-bulkhead-polypropylene-avantor)
Male luer (1/16" barb; pack of 25) | VWR | MFLX45504-00 | 1 | £20.40 | £20.40 | VWR (https://uk.vwr.com/store/item/EU7104664/masterflex-adapter-fittings-male-luer-to-hose-barb-straight-polycarbonate-avantor)
Luer stopcock (pack of 10) | VWR | MFLX30600-02 | 1 | £34.60 | £34.60 | VWR (https://uk.vwr.com/store/item/EU7103411/masterflex-luer-stopcock-fittings-polycarbonate-avantor)
Threaded Luer (pack of 25) | VWR | MFLX45508-30 | 1 | £28.90 | £28.90 | VWR (https://uk.vwr.com/store/item/EU7104706/masterflex-adapter-fittings-female-luer-to-hose-barb-bulkhead-polypropylene-avantor)
Prices correct 10/2024 | | Total | | | £470.80
Total Price | £2,504.79

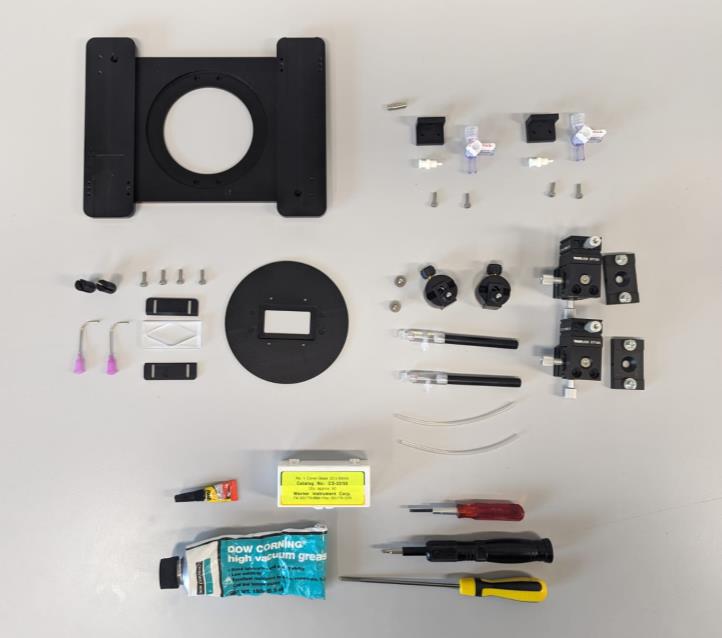
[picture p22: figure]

BUILDING THE VASOTRACKER BATH | PAGE | 5

## Building the VasoTracker Bath

Step by Step Guide

### 1. Gather your supplies

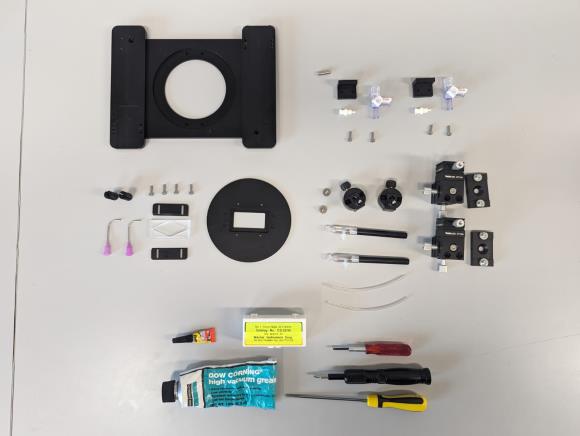
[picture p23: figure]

### 2. Attach magnets: Secure magnets into the baseplate and chamber base using superglue (8

magnets in total,4 in baseplate, and 4 in chamber base). Ensure correct orientation of the magnets!

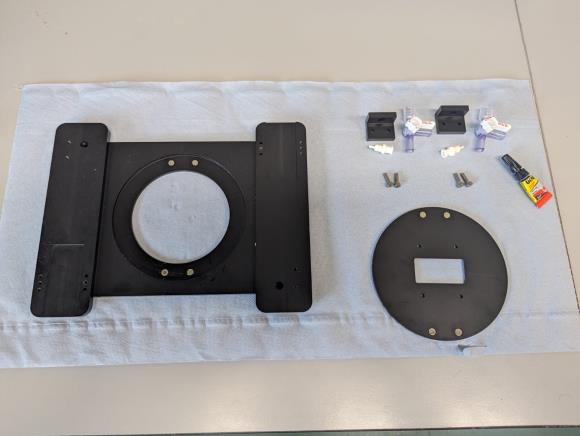
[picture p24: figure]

3. Mount the tubing connectors: attach one on each side of the bath using M3 screws. Connect a threaded leur and stopcock to each.

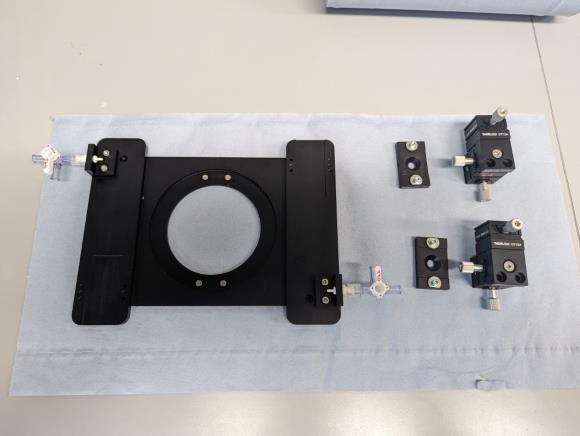
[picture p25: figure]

4. Attached the 3-axis positioners onto the baseplate.
- 4A. Remove the base from each positioner. Keep the screw assemblies!

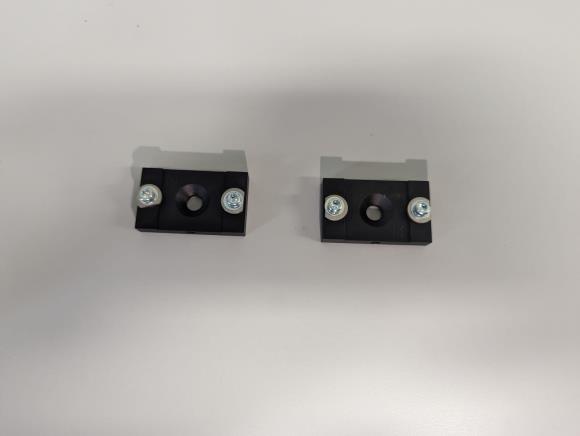
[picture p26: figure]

- 4B. Rotate the nuts on the screws so that the narrow end is facing the screw cap.

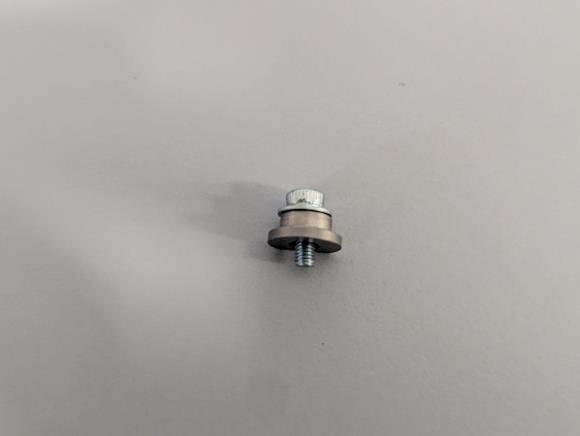
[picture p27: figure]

- 4C. Mount the four screw assemblies onto the baseplate. Do not tighten fully.

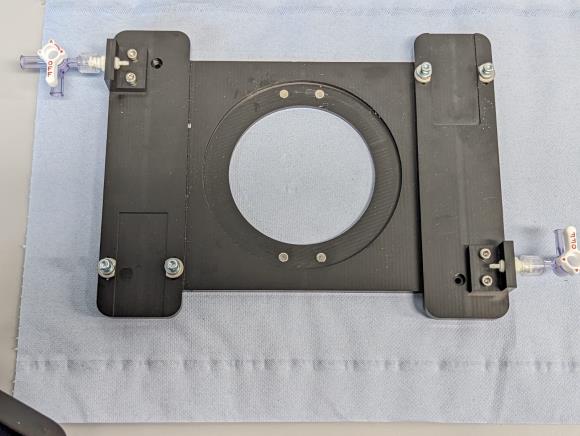
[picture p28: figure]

- 4D. Slide each of the positioners into position. Secure each using the four screws.

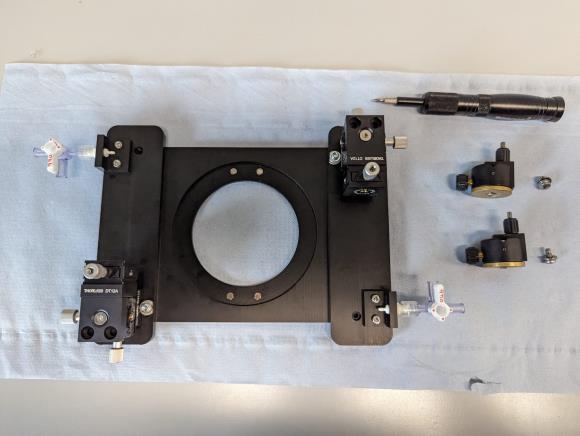
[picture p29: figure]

- 4E. Disassemble the rotatable probe clamps then mount one to each of the positioners:

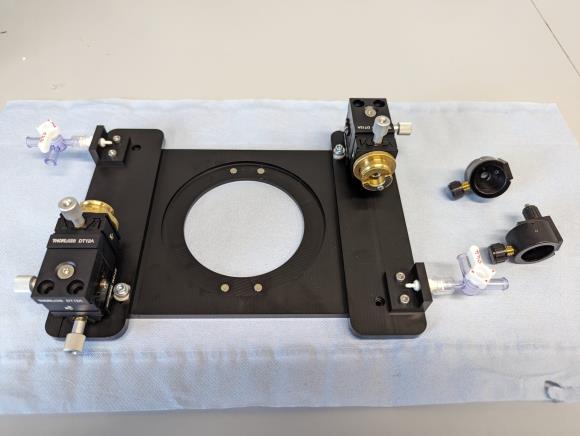
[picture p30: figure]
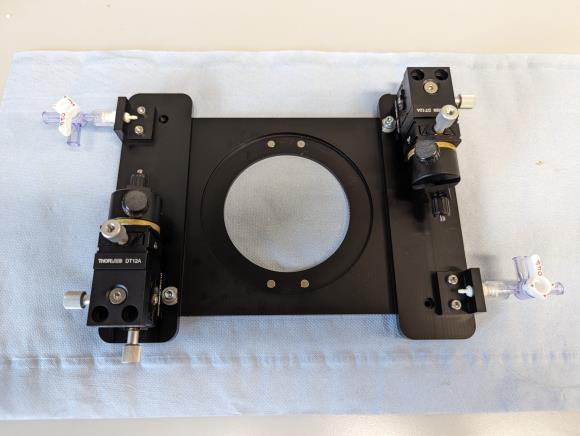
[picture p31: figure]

5. Prepare the bath chamber: mount a coverslip to the bath chamber using vacuum grease.

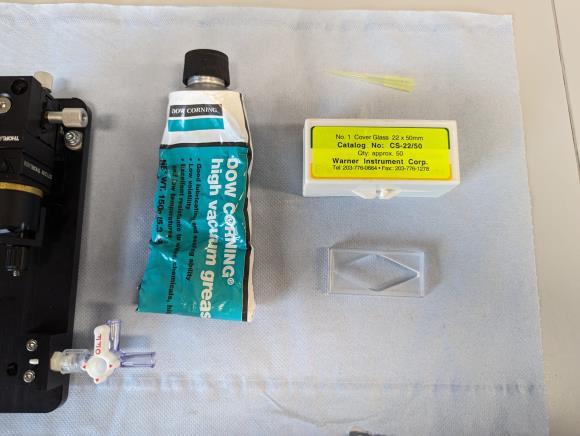
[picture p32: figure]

6. Place the chamber base into the baseplate (the magnets will snap it into place). Then mount the chamber in the center and secure with the screw clamps.

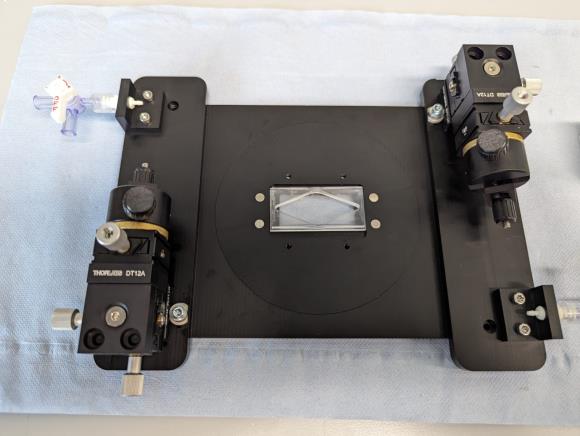
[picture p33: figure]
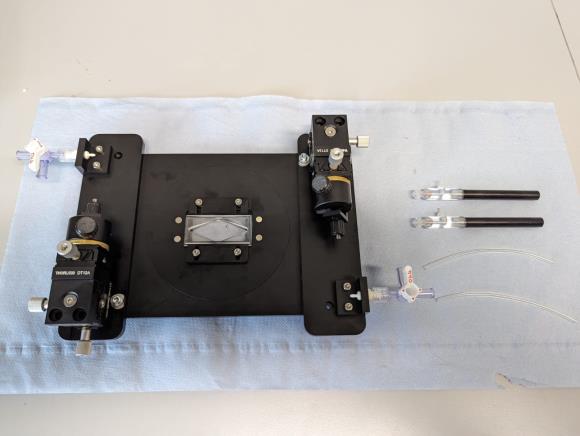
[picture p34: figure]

7. Attach the cannula holders to the rotatable clamps.

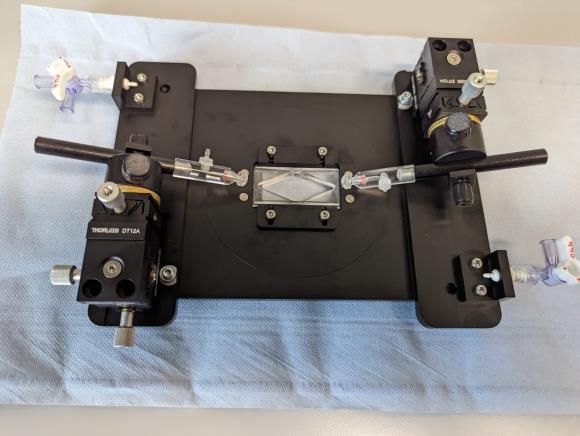
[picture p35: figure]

8. Connect the cannula holders to the luer tubing connectors. Use either 1.22 mm for a lower dead volume, but 1.52 mm inner diameter tubing also works.

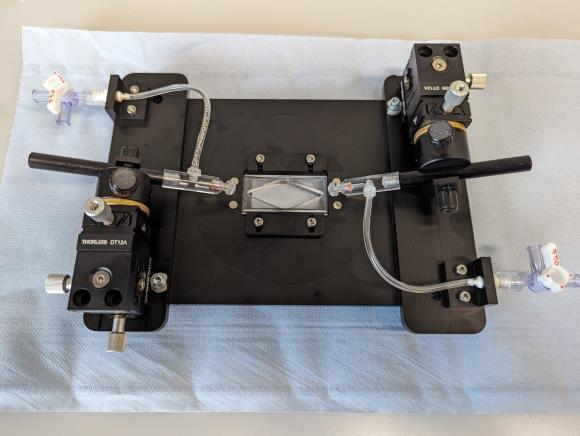
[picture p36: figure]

9. Insert pulled glass cannula (1.5 mm OD; matched to specific cannula holders) and center in the bath.

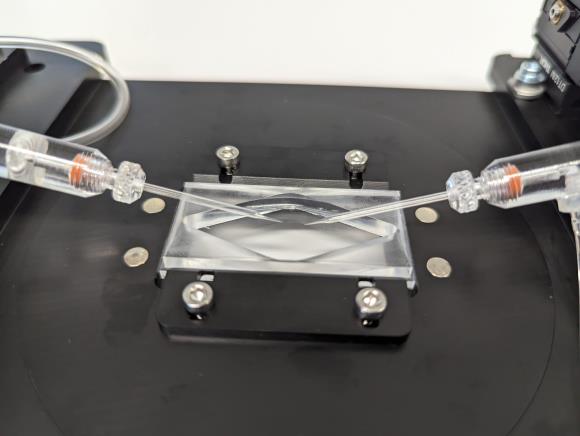
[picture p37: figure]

10. Attach perfusion plumbing holder. Glue magnets into the bottom of the 3D printed perfusion plumbing holders and mount onto the bath.

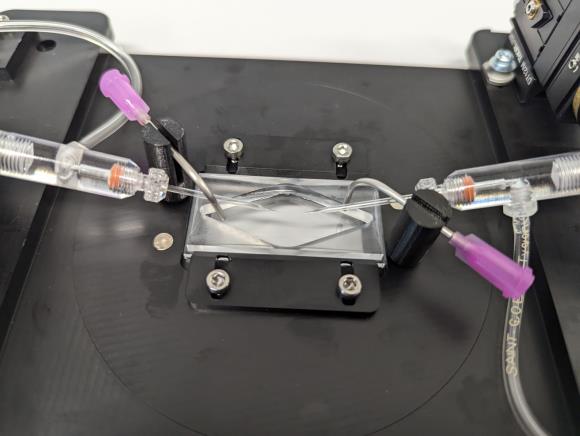
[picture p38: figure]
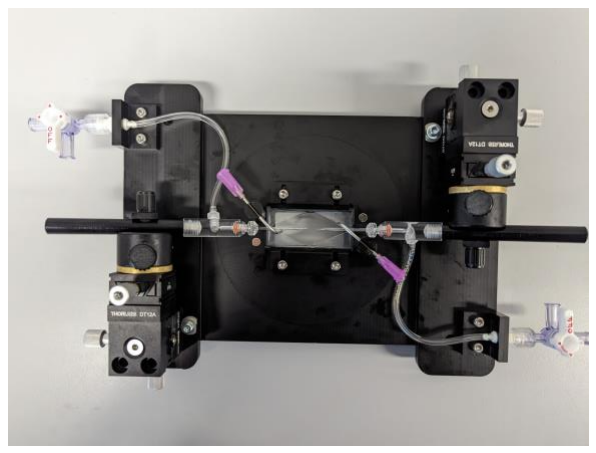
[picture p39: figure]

### 11. Perform some experiments with your new VasoTracker bath!

Replacing the Glass Cannula

12. Remove the Cannula Holder from the Chamber:
- Loosen the rotatable clamp securing the cannula holder and gently rotate it out of the bath chamber.

Tip: Detaching the tubing connected to the cannula holder may facilitate easier removal.

13. Stabilize the Cannula Holder:
- Once the cannula holder is removed from the bath, tighten the rotatable clamp to hold it securely in the horizontal position.
14. Remove the Old Glass Cannula:
- Loosen the thumb screw on the cannula holder and carefully remove the old cannula.
15. Prepare a New Glass Cannula:
- Use a pipette puller (e.g., Sutter P-97) to pull a new glass cannula to the appropriate dimensions.
- Adjust the Length: Trim the new cannula to the appropriate length.

Tip: Score the cannula with a diamond-tipped scribe before snapping to achieve a clean end. Fire polish the end with a flame for smoothness. Cutting the new cannula to a length similar to the old one simplifies realignment in the chamber.

16. Insert the New Cannula:
- Gently insert the new cannula into the holder and secure it by tightening the thumb screw.
17. Reinsert the Cannula into the Bath Chamber:
- Loosen the rotatable clamp, carefully rotate the cannula holder back into the bath chamber, and ensure the new cannula does not contact the bottom of the chamber.

Tip: Under a dissection microscope, use the VasoTracker 3-axis positioners to precisely realign the cannula in the center of the bath.

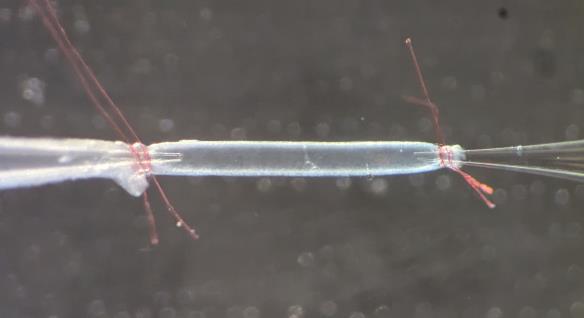
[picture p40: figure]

PREPARATION OF ISOLATED BLOOD VESSELS | PAGE | 12

## Preparation of Isolated Blood Vessels

PREPARATION OF ISOLATED BLOOD VESSELS | PAGE | 13

Mounting the Vessel onto the Cannula

### 1. Prepare the bath chamber:

- Fill the bath chamber with your physiological saline of choice.
- Flush the tubing/cannula with physiological saline using a 5ml syringe attached to the leur stopcocks. Leave the syringe attached to one of the cannula (you will mount the first end of your vessel on this cannula).

### 2. Prepare Ties:

- Cut enough threads or fine suture material for both ends of the vessel. Loop one or two suture threads over the first cannula in advance to simplify attachment.

Tip: A double overhand knot provides more stability than a single knot. Using two threads on each end can further enhance stability. Some people use suture threads, but we like to pull apart cotton thread and use individual strands for our ties.

### 3. Tie vessel onto first cannula:

- Gently cannulate one end of the vessel, securing it to the cannula with your ties.

Tip: If possible, leave a small piece of fat or branch attached to the vessel. This allows you to maneuver the vessel by gripping the fat/branch with forceps, helping to avoid potential damage to the vessel itself.

### 4. Flush blood from the vessel lumen:

- Use the attached syringe, very gently flush the lumen of the vessel to remove any blood.

### 5. Prepare the second cannula:

- Align the second cannula with the other end of the blood vessel and loop one or two ties over it.
- Ensure the luer stopcock is in the closes position.

### 6. Attach the vessel to the second cannula:

- Mount the vessel onto the second cannula, position the suture threads over the vessel and cannula, and secure by tightening.

### 7. Straighten the Vessel:

- Gently pressurize the blood vessel and use the 3-axis positioners to straighten the vessel without stretching it.

Tip: With a bit of practice, you can perform this step with a syringe. But inexperienced users should pressurize the vessel using a pressure servo system, or gravity-driven pressure control. See next step.

PREPARATION OF ISOLATED BLOOD VESSELS | PAGE | 14

Pressurizing the Vessel

1. Place the myograph chamber on your microscope stage:
- It may be useful to visualize the vessel using the VasoTracker software.
2. Connect the Pressure Control:
- Connect your pressure control system (servo or gravity-driven) to the 3-way valves. Keep the valves (on the chamber) closed initially, allowing physiological saline to flow through the tubing, and the open end of the valve not heading to the vessel, into a waste receptacle

Tip: Flowing saline through the pressure system ensures that air bubbles are removed from the system. If any get stuck in the tubing, give it a tap to dislodge and allow enough saline to flow through to remove any air bubbles.

3. Start Perfusion and Temperature Control:
- Connect the inflow and outflow tubing for perfusate circulation and temperature monitoring. Start the perfusate system and maintain the temperature using your chosen control method.
4. Pressure Adjustment:
- Using either manual or automated control (using VasoTrackers automated pressure control, see VasoTracker software), gradually increase the pressure.
- Begin with low pressure (~20 mmHg) and increase to the desired experimental pressure, typically 60 - 120 mmHg, depending on the vessel type and study objective, at 10-20 mmHg increments, allowing a 5-minute equilibration between each increment.
5. Monitor Vessel Diameter:
- Use the VasoTracker software to track the vessel’s diameter throughout the pressurization process.
- The vessel may need to be stretched (using the 3-axis positioner) to ensure it is not kinked or curved.
6. Check for Leaks and Adjustments:
- Once at the desired pressure, close of the vessel by closing both 3-way valves. The diameter should remain stable. A decrease in diameter indicates a leak in the system. If there is a leak:
- Ensure all tubing connections are tight and there are no visible leaks.
- Ensure the ties attaching the vessel to the cannula are tight and with no leaks.
- Visibly inspect the vessels for any leaks, this may indicate damage to the vessel or small branches.

PREPARATION OF ISOLATED BLOOD VESSELS | PAGE | 15

Checking the viability of the blood vessel

Once the vessel reaches the target pressure and diameter, leave to equilibrate for 30 – 60 minutes and then perform a viability check before continuing with any experiment. The steps below are one example viability protocol, but there are many other suitable procedures (e.g. using a depolarizing saline containing a high concentration of K+)

1. Induce Contraction with Phenylephrine (PE):
- Add enough phenylephrine to the perfusate bath to reach a final circulating concentration of 1 µM, and constrict the blood vessel.
- Allow the vessel to contract fully until a stable plateau is reached.
2. Wash with PSS:
- Wash the PE out using PSS buffer until the vessel returns to its baseline diameter.
- Repeat the PE contraction to confirm reproducible contraction responses.
3. Assess Endothelial Function with Acetylcholine (ACh):
- Once the vessel reaches the contracted state with PE, add acetylcholine (ACh) to reach a final circulating concentration of 1 µM.
- Allow the vessel to dilate fully until a stable plateau is reached. Measure the level of vasodilation.
4. Wash with PSS:
- Wash the PE and ACh out using PSS buffer until the vessel returns to its baseline diameter.
5. Ready for Experimental Use:
- Assess the level of vasoconstriction/vasodilation achieved, and if acceptable then continue with your experiments. If the responses are not acceptable, it is time to get a new vessel mounted.

Tip: VasoTracker software makes it easy to assess percentage vasoconstriction and percentage vasodilation. Simply set the “reference diameter” at the beginning of your viability test and VasoTracker software will display the current diameter as a percentage of this reference value.


www.vasotracker.com

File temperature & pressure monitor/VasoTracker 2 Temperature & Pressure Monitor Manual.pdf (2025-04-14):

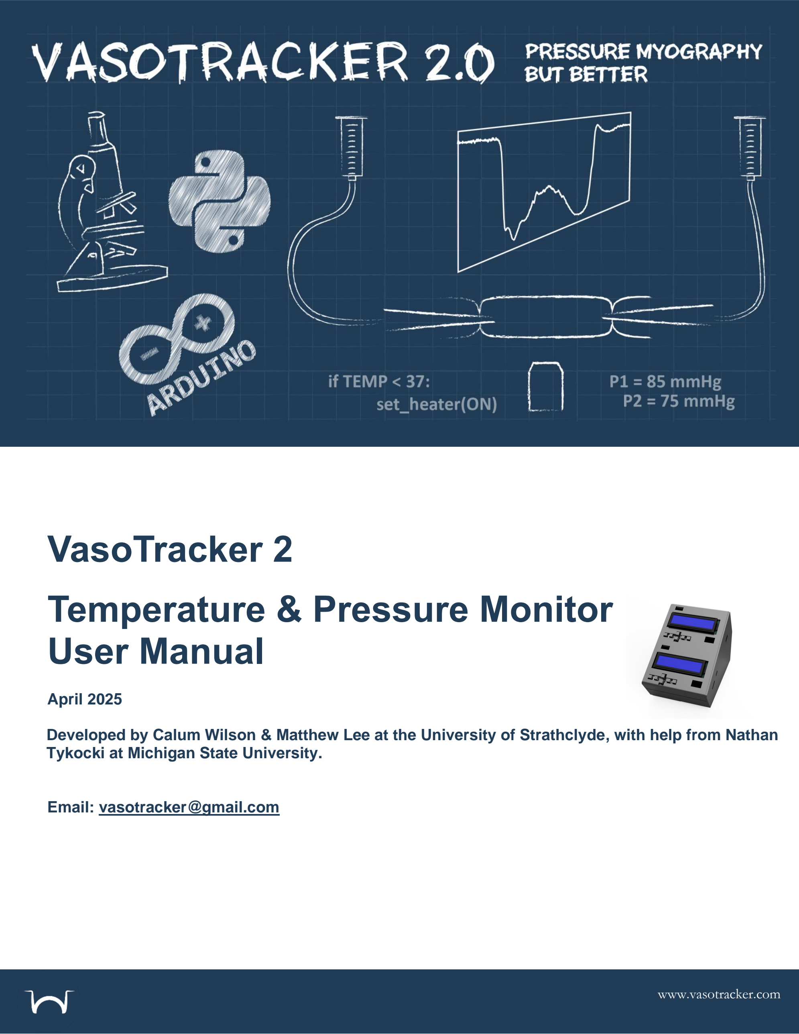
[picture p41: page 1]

# VasoTracker 2

# Temperature & Pressure Monitor User Manual

April 2025

Developed by Calum Wilson & Matthew Lee at the University of Strathclyde, with help from Nathan Tykocki at Michigan State University.

Email: vasotracker@gmail.com

www.vasotracker.com

## Table of Contents

Option 1: Using the A000077 Protoshield
Option 2: Using the Sparkfun Protoshield Programming the VasoTracker Temperature Monitor

Pressure Monitor Connections and Wiring Wheatstone Bridge Shield Connections Wheatstone Bridge Shield Setup Mapping transducer Connections
Stacking the Arduino Shields
Programming the VasoTracker Temperature Monitor Integrating the Temperature and Pressure

OVERVIEW | PAGE | 1

## Overview

PARTS LIST | PAGE | 2

## Parts List

VasoTracker Temperature & Pressure Monitor Parts

3D Printed Parts

3D Printed Enclosure | VasoTracker | - | 1 | £0 | £0 | GitHub (https://github.com/VasoTracker/VasoTracker-2)
Prices correct 10/2024 | | Total | | | £0.00

VasoTracker Temperature Monitor

Component | Supplier | Product # | Qty | Price | Total | Supplier Link
Arduino Uno** | Arduino | RB-Ard-34 | 1 | £26.50 | £26.50 | RobotShop (https://uk.robotshop.com/products/arduino-uno-r3-usb-microcontroller)
12V power supply | RS | 903-7048 | 1 | £8.33 | £8.33 | RS (https://uk.rs-online.com/web/p/ac-dc-adapters/1753303)
Arduino Proto Shield | Skinflint | A000077 | 1 | £13.50 | £13.50 | SkinFlint (https://skinflint.co.uk/arduino-proto-shield-uno-a000077-a799462.html)
LCD Shield | RobotShop | RB-Cyt-73 | 1 | £3.64 | £3.64 | RobotShop (https://uk.robotshop.com/products/cytron-lcd-keypad-shield-arduino)
10k NTC Thermistor | Adafruit | 372 | 1 | £3.06 | £3.06 | DigiKey (https://www.digikey.co.uk/en/products/detail/adafruit-industries-llc/372/6051772)
Resistor kit | RobotShop | RES-E12 | 1 | £13.80 | £13.80 | RobotShop (https://uk.robotshop.com/products/resistor-kit-610pk)
Jumper wire kit | RobotShop | RB-Cix-02 | 1 | £3.77 | £3.77 | RobotShop (https://uk.robotshop.com/products/140-piece-pre-formed-jumper-wire-kit)
2-pin Screw Terminal | RobotShop | RB-Dfr-465 | 1 | £0.76 | £0.76 | RobotShop (https://uk.robotshop.com/products/2-pin-screw-terminal-35mm)
Prices correct 10/2024 | | Total | | | £73.36

VasoTracker Pressure Monitor

Component | Supplier | Product # | Qty | Price | Total | Supplier Link
Arduino Uno** | Arduino | RB-Ard-34 | 1 | £26.50 | £26.50 | RobotShop (https://uk.robotshop.com/products/arduino-uno-r3-usb-microcontroller)
12V power supply | RS | 903-7048 | 1 | £8.33 | £8.33 | RS (https://uk.rs-online.com/web/p/ac-dc-adapters/1753303)
Wheatstone bridge amplifier shield | RobotShop | RB-Onl-38 | 1 | £45.63 | £45.63 | RobotShop (https://www.robotshop.com/uk/strain-gauge-load-cell-amplifier-shield-2ch.html)
LCD Shield | RobotShop | RB-Cyt-73 | 1 | £3.64 | £3.64 | RobotShop (https://uk.robotshop.com/products/cytron-lcd-keypad-shield-arduino)
Inline pressure transducers | Honeywell | 26PCDFG5G | 2 | £74.55 | £149.10 | Mouser (https://www.mouser.co.uk/ProductDetail/Honeywell/26PCDFG5G/)
12” 4-pin jumper wire | RobotShop | RB-Spa-1107 | 2 | £0.60 | £1.20 | RobotShop (https://uk.robotshop.com/products/12-4-pin-jumper-wire)
Arduino stackable headers | RobotShop | RB-Spa-928 | 1 | £1.67 | £1.67 | RobotShop (https://uk.robotshop.com/products/arduino-r3-stackable-headers)
Female to female jumper | RobotShop | RB-Gog-65 | 1 | £4.31 | £4.31 | RobotShop (https://uk.robotshop.com/products/assorted-silicon-wire-jumper-22-awg-65pk-f-f)
Heatshrink tubing | RobotShop | RB-Gog-47 | 1 | £1.92 | £1.92 | RobotShop (https://uk.robotshop.com/products/shrink-tube-variety-pack)
Prices correct 10/2024 | | Total | | | £242.30
Total Price | | | | | £315.66

The software and instructions provided only work for Arduino Uno boards with the ATMega microcontroller chip. Other variants (e.g., SAMD51 or ESP-32 chips) cannot be used.

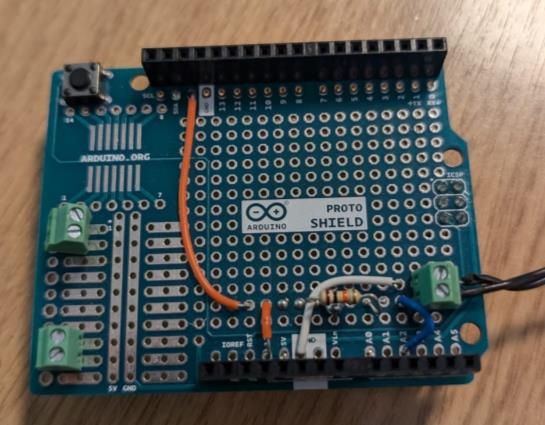
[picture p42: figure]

BUILDING THE VASOTRACKER TEMPERATURE MONITOR | PAGE | 3

## Building the VasoTracker Temperature Monitor

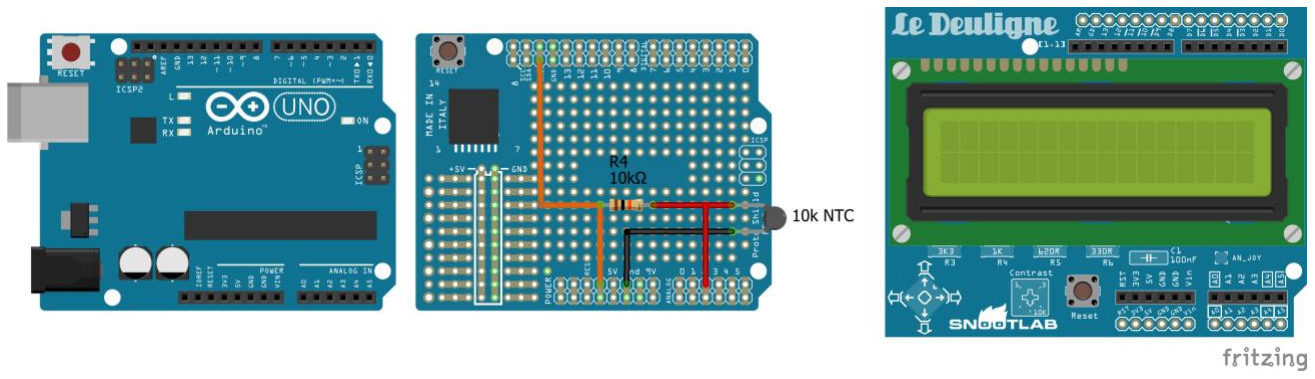
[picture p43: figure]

BUILDING THE VASOTRACKER TEMPERATURE MONITOR | PAGE | 4

Option 1: Using the A000077 Protoshield

The temperature monitor uses a simple voltage divider to convert the thermistor resistance (and thus temperature) to voltage

Figure 1 – The VasoTracker 2.0 Temperature Monitor Wiring Diagram

1. Build the temperature sensor circuit on the Arduino Proto shield.
2. Stack the completed Proto shield on top of the Arduino Uno.
3. Stack the LCD shield on top of the Arduino Uno.
4. (Optional) 3D print an enclosure to protect your VasoTracker pressure monitor. You can place the device in its own enclosure or use the dual enclosure designed for VasoTracker 2.0. The STL files for the enclosure below can be found on the VasoTracker 2 GitHub. (https://github.com/VasoTracker/VasoTracker-2)

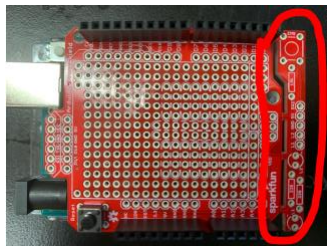
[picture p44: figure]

BUILDING THE VASOTRACKER TEMPERATURE MONITOR | PAGE | 5

Option 2: Using the Sparkfun Protoshield

If you struggled to source the A000077 Protoshield, you may have purchased the Sparkfun version…

1. Snap off the test part of the sparkfun board It’s not needed.
2. Build circuit by soldering the wires/components into place.

### 3. Ensure wires/components are connected using solder bridges on the bottom side of the

protoboard.

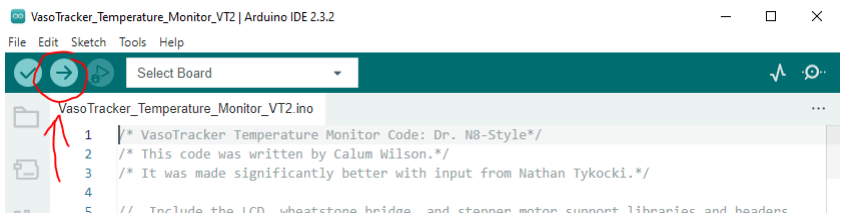
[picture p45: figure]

BUILDING THE VASOTRACKER TEMPERATURE MONITOR | PAGE | 6

Programming the VasoTracker Temperature Monitor

1. Step 1: Download and install the Arduino IDE. (https://www.arduino.cc/en/Guide/Windows#toc1) This can be done using either Windows or Mac OSX; however, the VasoTracker software installer only runs in Windows.

If you want to run VasoTracker on iOS then you must install from the source code. Instructions for doing so can be found in the VasoTracker Software User Manual

2. Download the latest VasoTracker Pressure Monitor Arduino code from GitHub. (https://github.com/VasoTracker/VasoTracker-2)

### 3. Unzip the “VasoTracker Temperature_Monitor_VT2” folder. The folder name must not be

changed.

4. Connect the Arduino to your computer using the Arduino USB cable.
5. Using the Arduino IDE software, open “VasoTracker_Temperature_Monitor_VT2.ino”.
6. Configure the Arduino IDE for your Arduino Uno.

### 7. Tools → Board → Arduino Uno 8. Tools → Port → COM X (Arduino Uno). “X” will vary by computer and system, depending on

how many USB peripherals are attached.

9. Step 7: Upload the code to the Arduino by clicking the upload button. No modifications to the code are required if you are doing a standard build as outlined above.

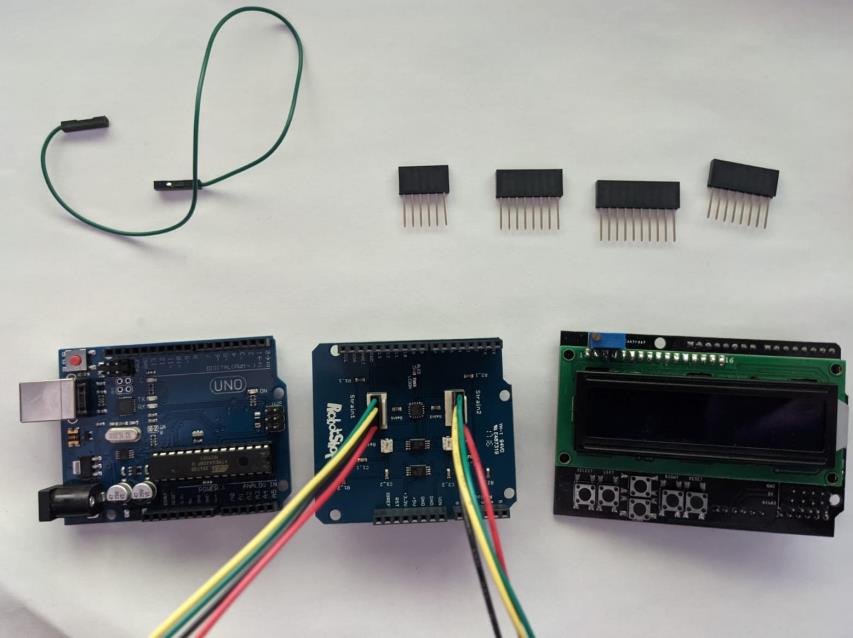
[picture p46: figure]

BUILDING THE VASOTRACKER PRESSURE MONITOR | PAGE | 7

## Building the VasoTracker Pressure Monitor

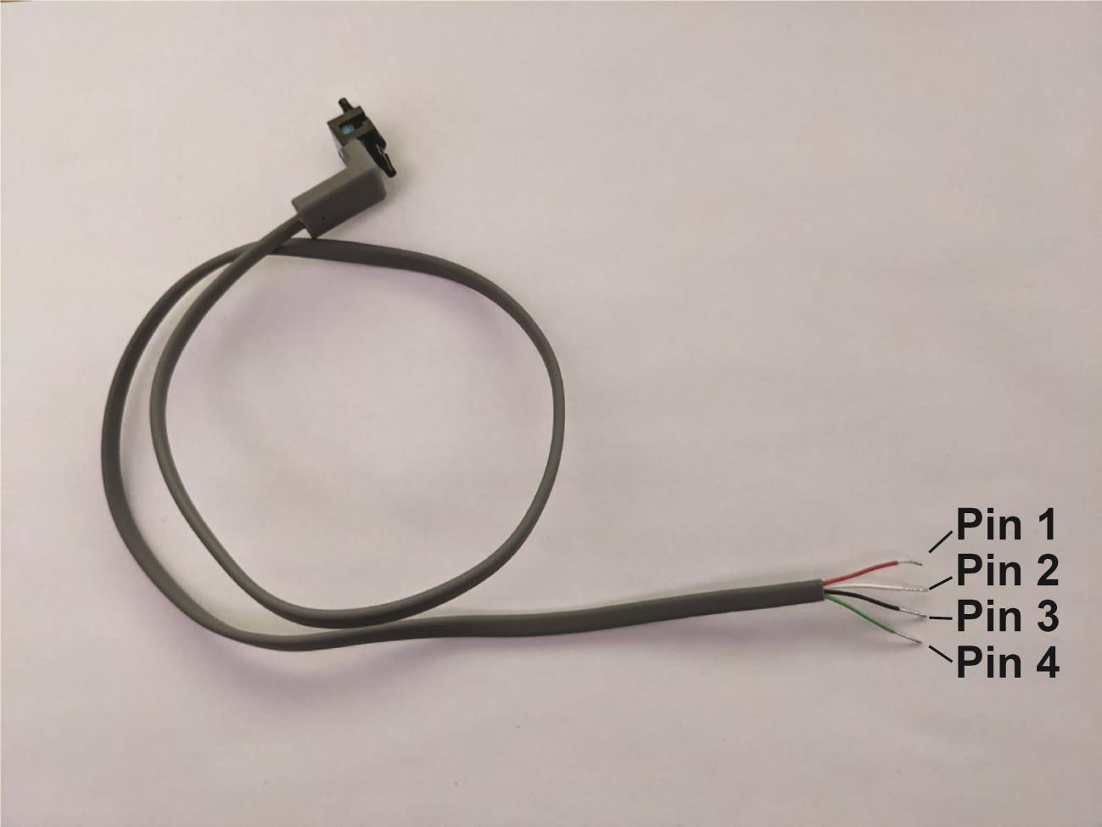
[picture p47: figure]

BUILDING THE VASOTRACKER PRESSURE MONITOR | PAGE | 8

Pressure Monitor Connections and Wiring

The 26PCDFG5G pressure transducer has four pins. This version of the sensor comes with a handy cable. There are four wires:

- | Pin 1 (Red wire): | Vs
- | Pin 2 (White wire): | Signal +
- | Pin 3 (Black wire): | Ground
- Pin 4 (Green wire): Signal -

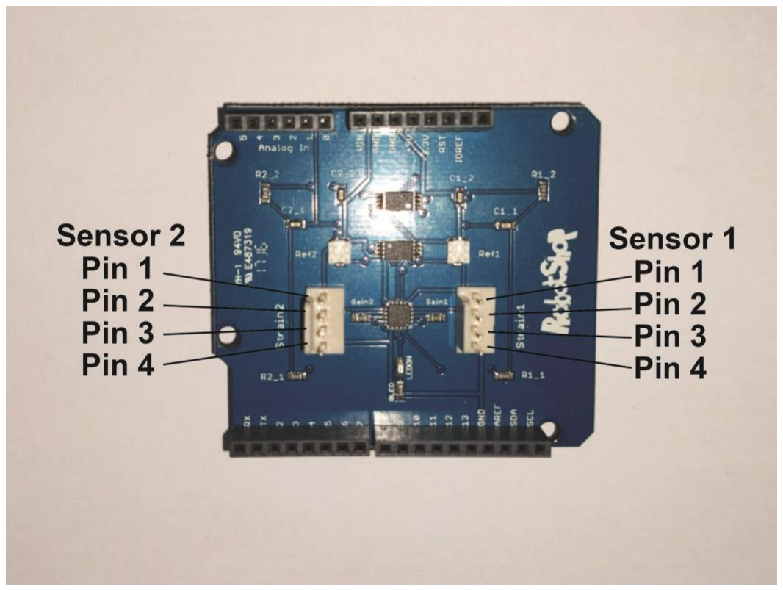
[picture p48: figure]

BUILDING THE VASOTRACKER PRESSURE MONITOR | PAGE | 9

Wheatstone Bridge Shield Connections

The following instructions are for use with the supplied Honeywell pressure transducer cable. There is a crossover within the cable header. If you make your own cable then the Pin order is different

The Wheatstone shield uses the following Arduino pins:

- A0: Sensor 1 input
- A1: Sensor 2 input
- 5V, 3.3V, GND: to power the shield

Each pressure sensor needs to be connected to one of the 4-pin Molex connectors on the Wheatstone bridge shield. The Molex pins are as follow:

- Molex Pin 1: Vs
- Molex Pin 2: Signal +
- Molex Pin 3: Signal -
- Molex Pin 4: Ground

Figure 2 – Wheatstone bridge pinout.

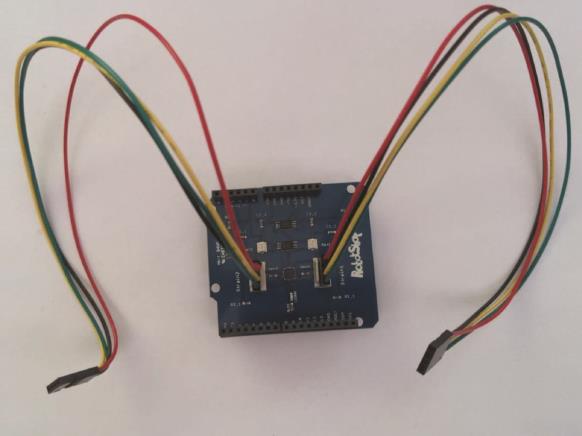
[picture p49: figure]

BUILDING THE VASOTRACKER PRESSURE MONITOR | PAGE | 10

Wheatstone Bridge Shield Setup

Each channel on the Wheatstone bridge shield has its own reference voltage that is set using specific channel potentiometers. Calibrating these is necessary to ensure that the shield works as intended.

- Documentation for the Wheatstone Bridge Shield can be found on the RobotShop website. (https://www.robotshop.com/en/strain-gauge-load-cell-amplifier-shield-2ch.html)
- Users need to perform the calibration procedure detailed in the “Test Procedure” pdf file (found here). (https://www.robotshop.com/media/files/pdf2/load_cell_shield_test-procedure.pdf)
- If you are too lazy to read this, then please turn both potentiometers fully clockwise, then turn back 1/4 - 1/8 of a turn so that the screw is parallel to the Arduino headers.
- https://www.robotshop.com/en/strain-gauge-load-cell-amplifier-shield-2ch.html
- The Wheatstone bridge shield contains two potentiometers

Mapping transducer Connections

The table below maps the pressure transducer connections to the Molex connector pins on the Wheatstone bridge shield:

Connection | Pressure sensor pin | Wheatstone bridge pin
Vss | Pin 1 (Red wire) | Molex Pin 1
Signal + | Pin 2 (White wire) | Molex Pin 2
Ground | Pin 3 (Black wire) | Molex Pin 4
Signal - | Pin 4 (Green wire) | Molex Pin 3

Table 1 - Mapping of pressure transducer connections to Wheatstone bridge shield

1. Connect the 4-pin jumper wires to the Molex connectors on the Wheatstone bridge.

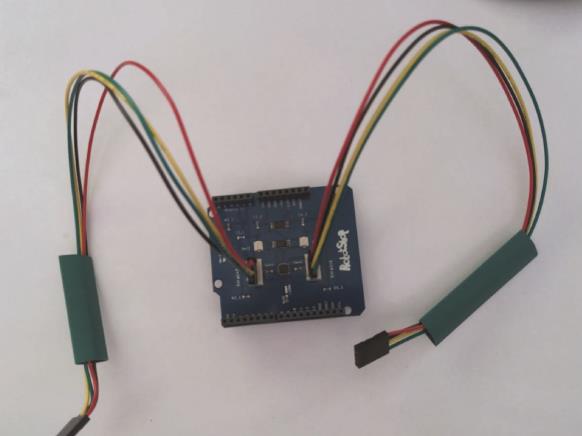
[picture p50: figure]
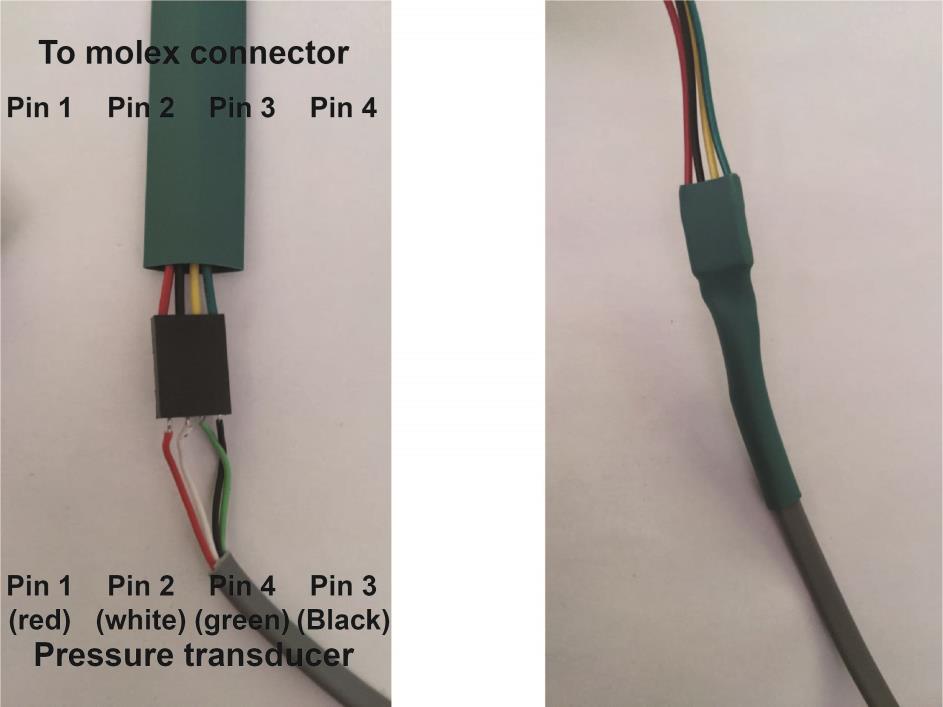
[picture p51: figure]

BUILDING THE VASOTRACKER PRESSURE MONITOR | PAGE | 11

### 2. Slide a piece of heatshrink tubing over the jumper wires

3. Connect the pressure transducer cable to the jumper wire as per Table 1.

### 4. Slide a piece of heat shrink tubing over the jumper wires. Heat gently (with heat gun

or soldering iron) to shrink. Be careful not to burn the heat shrink tubing or damage the wiring insulation.

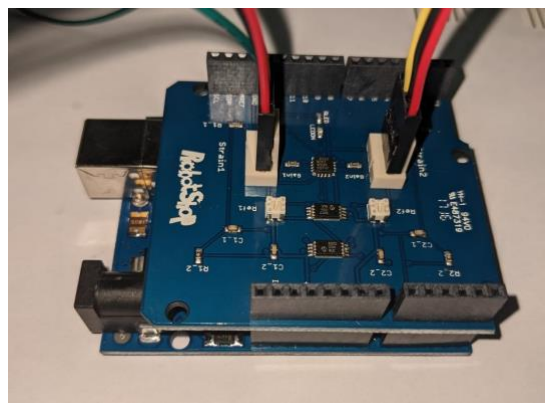
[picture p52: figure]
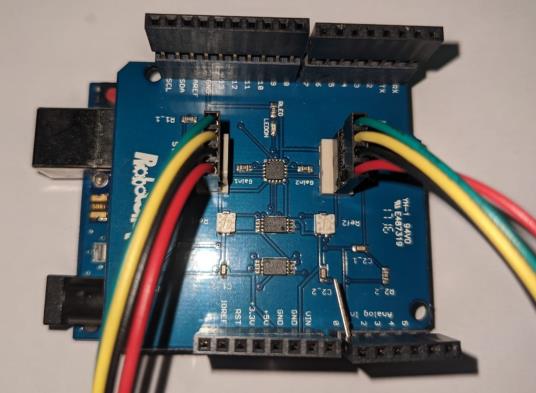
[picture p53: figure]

BUILDING THE VASOTRACKER PRESSURE MONITOR | PAGE | 12

Stacking the Arduino Shields

1. Gather the Arduino, shields, and stackable headers.
2. Stack the wheatstone bridge shield on top of the Arduino Uno.

### 3. Place stackable headers on top of the Wheatstone Amplifier Shield. These provide

clearance for the pressure transducer connections). Bend the A0 pin on the stackable header so that it does not connect to the Arduino Uno board (see Figure 8).

The LCD shield normally uses the A0 pin for the button commands. However, the strain guage also uses the A0 (and A1) inputs on the Arduino. To get around this problem, we route the LCD A0 pin to A5.

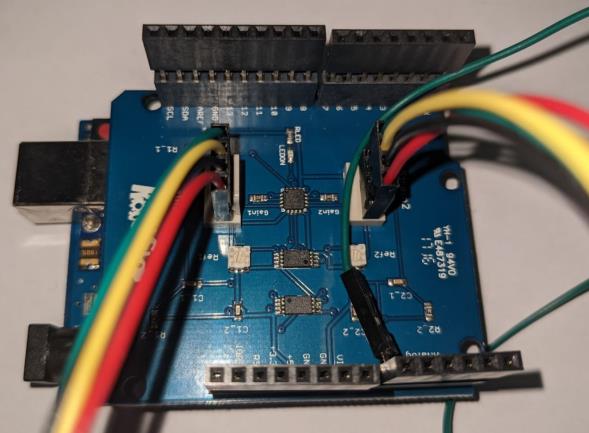
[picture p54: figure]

BUILDING THE VASOTRACKER PRESSURE MONITOR | PAGE | 13
4. Connect the jumper cable to the bent A0 pin.
5. Stack the LCD shield on top of the headers. Route the jumper cable to the A5 pin.

Alternative method for rerouting LCD pins: Remove the A0 pin from the LCD shield (heat it up with a soldering iron and pull it out using pliers). Solder a jumper wire from A0 to A5 on the board. This is a better way to do the above.

6. (Optional) 3D print an enclosure to protect your VasoTracker pressure monitor. STL files for a single enclosure can be found on the VasoTracker 2 GitHub. (https://github.com/VasoTracker/VasoTracker-2) Instructions for connecting the Temperature and Pressure Monitors in a single enclosure are available here.


BUILDING THE VASOTRACKER PRESSURE MONITOR | PAGE | 14

Programming the VasoTracker Temperature Monitor

1. Download and install the Arduino IDE. (https://www.arduino.cc/en/Guide/Windows#toc1) This can be done using either Windows or Mac OSX; however, the VasoTracker software installer only runs in Windows.

If you want to run VasoTracker on iOS then you must install from the source code. Instructions for doing so can be found in the VasoTracker Software User Manual

2. Download the latest VasoTracker Pressure Monitor Arduino code from GitHub. (https://github.com/VasoTracker/VasoTracker-2)

### 3. Unzip the “VasoTracker_Pressure_Monitor_VT2” folder. You must keep all the files in

this folder together, and the folder name must not be changed.

4. Connect the Arduino to your computer using the Arduino USB cable.

### 5. Within the “VasoTracker_Pressure_Monitor_VT2” folder, you will find three files: (1)

“pressure.cpp”; (2) “pressure.h”; and (3) “VasoTracker_Pressure_Monitor_VT2.ino”. Using the Arduino IDE software, open “VasoTracker_Pressure_Monitor_VT2.ino”.

6. Configure the Arduino IDE for your Arduino Uno. If you purchased an Arduino Uno clone board (e.g., Adafuit Metro, please see the instructions for configuring the board at the supplier’s website).
- Tools → Board → Arduino Uno
- Tools → Port → COM X (Arduino Uno). “X” will vary by computer and system, depending on how many USB peripherals are attached.

### 7. Upload the code to the Arduino by clicking the upload button. No modifications to the

codee are required if you are doing a standard build as outlined above.


INTEGRATING THE TEMPERATURE AND PRESSURE MONITOR | PAGE | 15

## Integrating the Temperature and Pressure Monitor


INTEGRATING THE TEMPERATURE AND PRESSURE MONITOR | PAGE | 16

The VasoTracker Temperature and Pressure Monitors can either be held as independent units, or can be enclosed in a single enclosure and powered from a single power supply.

### 1. Download the VasoTracker 2 CombiBox and 3D print all of the parts (including two

sets of buttons).

2. Slide the Arduino from the Temperature Monitor into the lower slot in the enclosure.

### 3. Slide the Arduino + Wheatstone Shield from the Pressure Monitor into the upper slot

in the enclosure.

### 4. Use jumper wires to connect the VIN and GND of the Wheatstone shield to that on the

Temperature Monitor Arduino. You may need to remove two pins from the stackable headers to achieve this.

5. Add the remaining shields to the Arduino’s (temperature monitor protoshield circuit, and LCDs). Use stackable headers to raise the height of the Pressure Monitor LCD.
6. Add the front plate and the buttons.
7. Power via the pressure monitor Arduino.

INTEGRATING THE TEMPERATURE AND PRESSURE MONITOR | PAGE | 17


SETTING UP THE VASOTRACKER PRESSURE MONITOR | PAGE | 18

## Setting up the VasoTracker Pressure Monitor


SETTING UP THE VASOTRACKER PRESSURE MONITOR | PAGE | 19

On first use, the VasoTracker pressure monitor needs to be calibrated. Once this has been done, the calibration values are saved into memory on the Arduino Uno and can be reloaded each time the pressure monitor is used – even after disconnecting the power. We recommend that you recalibrate the sensors once a week. We use a Big Ben manometer, but any calibrated manometer will suffice, such as a blood pressure cuff (with the cuff removed).

1. Use your tubing and connectors of choice to connect the first transducer to the manometer.
2. On the recalibrate screen (Figure 15), use the up/down buttons until the screen reads “YES” and press the “ENTER” button (left most on LCD screen).

SETTING UP THE VASOTRACKER PRESSURE MONITOR | PAGE | 20
3. The next screen is used to set the low pressure used for calibration (Figure 16). Use the UP/DOWN (10 mmHg increments) or left/right buttons (1 mmHg increments) to set the low calibration pressure to 0 mmHg. Save this value by pressing “ENTER”.
4. The next screen shows the reading from the pressure sensor (Figure 17). Ensure the manometer is set to the pressure set in the previous step (0 mmHg). Press “ENTER” to save this value.
5. The next screen is used to set the high pressure used for calibration (Figure 18). Use the UP/DOWN (10 mmHg increments) or left/right buttons (1 mmHg increments) to set the high calibration pressure to 160 mmHg. Save this value by pressing “ENTER”.


SETTING UP THE VASOTRACKER PRESSURE MONITOR | PAGE | 21
6. The next screen shows the reading from the pressure sensor (Figure 19). Ensure the manometer is set to the pressure set in the previous step (160 mmHg). Press “ENTER” to save this value.
7. Repeat Steps 3-6 for the second pressure transducer.
8. Connect the pressure sensors to your pressure myograph system and use with VasoTracker. If used with VasoTracker pressure myograph software, the pressure values with be saved along with blood vessel diameter data.


www.vasotracker.com

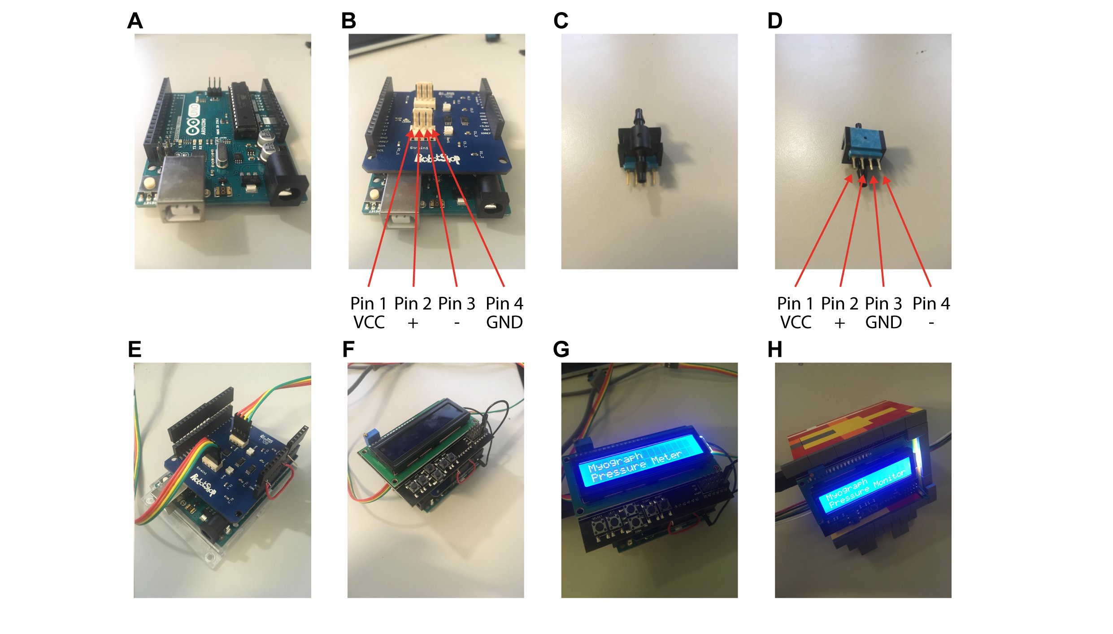
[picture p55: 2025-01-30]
temperature & pressure monitor/Images/Pressure Monitor Construction.jpg

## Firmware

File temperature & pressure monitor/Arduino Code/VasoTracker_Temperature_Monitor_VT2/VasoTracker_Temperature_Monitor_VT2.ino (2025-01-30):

/* VasoTracker Temperature Monitor Code: Dr. N8-Style*/
/* This code was written by Calum Wilson.*/
/* It was made significantly better with input from Nathan Tykocki.*/

//  Include the LCD, wheatstone bridge, and stepper motor support libraries and headers
#include <LiquidCrystal.h> // Include the LCD library

// Initialize the library with the numbers of the interface pins
//LiquidCrystal lcd(8, 9, 4, 5, 6, 7); 

//Shitty ebay LCD panels
// fill in aduino pin #s used to control LCD
const int rs=8; // arduino pin connect to LCD RS pin
const int en=9; // arduino pin connect to LCD Enable pin
const int d4=4;  // arduino pin connected to LCD data bit 4 pin
const int d5=5;  // arduino pin connected to LCD data bit 5 pin
const int d6=6;  // arduino pin connected to LCD data bit 6 pin
const int d7=7;  // arduino pin connected to LCD data bit 7 pin

LiquidCrystal lcd(rs, en, d4, d5, d6, d7); // constructor to initialize pins in library


#define btnRIGHT 0
#define btnUP 1
#define btnDOWN 2
#define btnLEFT 3
#define btnSELECT 4
#define btnNONE 5
#define btnUNKNOWN 6

// Initialize the thermistor values
#define thermistor_pin A2 // which analog thermistor input pin // Normally A0 or A2
#define nominal_temp 25 // nominal resistance temperature (almost always 25 C)   
#define nominal_resistance 10000 // nominal  resistance at nominal resistance temperature   
#define beta_coeff 3950 // beta coefficient of the thermistor
#define series_resistor 10000 // the value of the 'other' resistor    
#define output_pin  3

//  Setup the data recording (data to be sent out, sampling rate)
//******************************************************************************************************************
  #define       NUMSAMPLES 5               //  Change this to alter the number of samples averaged.                *
  unsigned long TIME_DELAY = 5;            //  Change this to alter the time delay for wheatstone bridge output.   *
  unsigned long LCD_TIME_DELAY = 500;      // Setting a delay to update the LCD screen

  #define initial_set_point 25.0 // initial set point
  int min_temp = 20;
  int max_temp = 40;
//******************************************************************************************************************


uint16_t      samples[NUMSAMPLES];      // Needed to determine how the samples will be summed and averaged.
unsigned long previousMillis = 0;        // Resetting the clock to determine how much time has elapsed.
unsigned long initMillis = 0;            // Resetting the clock to determine how much time has elapsed.
unsigned long elapsedMillis = 0;
bool update_flag = 0;                    // Flag to update the LCD display
double setpoint, test, cal_temp_low;


// Function for reading the keypad
int readkeypad(){
  int adc_key_in = analogRead(A0); //Normally 5 or 0
  int ret = btnUNKNOWN;
  
  if (adc_key_in < 50) ret = btnRIGHT;
  if ( (adc_key_in > 50) && (adc_key_in < 250) ) ret = btnUP;
  if ( (adc_key_in > 250) && (adc_key_in < 450) ) ret = btnDOWN;
  if ( (adc_key_in > 450) && (adc_key_in < 650) ) ret = btnLEFT;
  if ( (adc_key_in > 650) && (adc_key_in < 850) ) ret = btnSELECT;
  if (adc_key_in > 850) ret = btnNONE; 
  return ret;
 }

void displayScreen(char row1[], char row2[])
{
  lcd.clear();
  lcd.setCursor(0, 0); lcd.print(row1);
  lcd.setCursor(0, 1); lcd.print(row2);
}

// Setup function
void setup()
{
  // Initialize LCD screen and intro
  lcd.begin(16, 2); displayScreen("VasoTracker", "Temp Monitor"); delay(3000);
  
  // Main screen
  displayScreen("", "Act (*C):  ");
  
  Serial.begin(9600);

  // Setpoint
  setpoint = initial_set_point;

  //Set the output pin
  pinMode(output_pin, OUTPUT);
}

// < Main program loop >
void temperature(bool update_flag, double setpoint) {
  uint8_t i;
  float ADC_average;
  float resistance;
  float temperature;
  unsigned long currentMillis = millis();
  
  if ((currentMillis - previousMillis) >= TIME_DELAY) {

    // Take readings
    for (i = 0; i < NUMSAMPLES; i++) {
      samples[i] = analogRead(thermistor_pin);
    }
  
    // Sum readings
    ADC_average = 0;
    for (i = 0; i < NUMSAMPLES; i++) {
      ADC_average += samples[i];
    }

    // Average the readings
    ADC_average /= NUMSAMPLES;
  
    // Convert the voltage drop over the thermistor to resistance using the Steinhart equation
    resistance = series_resistor / ((1023 / ADC_average) - 1);
    temperature = 1 / (log(resistance / nominal_resistance) / beta_coeff + (1.0 / (nominal_temp + 273.15))) - 273.15;            

    // Ensure the "VasoTracker Temp" label is always displayed
    lcd.setCursor(0, 0); 
    lcd.print("VasoTracker Temp");

    // Update temperature reading only when the flag is set
    if (update_flag == 1) {
      lcd.setCursor(11, 1); // Update the temperature on the second line
      lcd.print(temperature);
    }

    // Print to the serial port in VasoTracker format
    Serial.print("<T1"); Serial.print(":"); Serial.print(temperature); Serial.print(";");
    Serial.print("T2"); Serial.print(":"); Serial.print(setpoint); Serial.print(";"); Serial.println(">");
  }
}







//If you want to do more things it's easy to add the loops here. Like if you wanted to do only 1 transducer and add temperature controls to a single unit...
unsigned long currentMillis_LCD = millis();
void loop(){
  
  //Get the current time
  currentMillis_LCD = millis();
  elapsedMillis = currentMillis_LCD - initMillis;

  // Check if we should update display
  if (elapsedMillis > LCD_TIME_DELAY){
    initMillis = currentMillis_LCD;
    update_flag = 1;
  


    // Check if any of the LCD shield buttons have been pressed
    int lcd_button_adc = analogRead(A0);
    int buttons2 = readkeypad();
    switch(buttons2){
      
      case btnUP:
        setpoint += 1;
        if(setpoint > max_temp)
          setpoint = max_temp;
        break;
        
      case btnRIGHT:
        setpoint += 0.5;
        if(setpoint > max_temp)
          setpoint = max_temp;
        break;
  
      case btnDOWN:
        setpoint -= 1;
        if(setpoint < min_temp)
          setpoint = min_temp;
        break;
  
      case btnLEFT:
        setpoint -= 0.5;
        if(setpoint < min_temp)
          setpoint = min_temp;
        break;
    }
   }

  // Get the current temperature
  temperature(update_flag, setpoint);
  update_flag = 0;
}

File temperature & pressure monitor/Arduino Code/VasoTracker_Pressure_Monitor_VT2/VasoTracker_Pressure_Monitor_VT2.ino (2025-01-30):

/* VasoTracker Pressure Monitor Code: Dr. N8-Style*/
/* This code was written by Calum Wilson with help from Penny Lawton.*/
/* It was made significantly better by Nathan Tykocki.*/
/* V4 additions/updates: 
1) removed extraneous functions, 
2) fixed EEPROM saving to include both transducers, 
3) changed from int to double to increase accuracy and prevent negative number overflow leading to max output error.
/* V4A additions/updates: 
1) Added running average to getValueADC()
2) Changed number of samples Added delay to all running averages to stop pressure jittering about
*/

//  Include the LCD, wheatstone bridge, and stepper motor support libraries and headers
#include <EEPROM.h>
#include <LiquidCrystal.h>
#include "pressure.h" //This file should be in the working folder. It now contains all the wheatstone bride headers and associated info (from here: https://github.com/RobotShop/Wheatstone-Bridge-Amplifier-Shield/archive/master.zip).

//  Initialize the library with the numbers of the interface pins
LiquidCrystal lcd(8, 9, 4, 5, 6, 7);

//  Initial calibration values for force transducer
int    CST_PRESSURE_IN_MIN = 100;       // Raw value calibration lower point
int    CST_PRESSURE_IN_MAX = 400;       // Raw value calibration upper point
double CST_PRESSURE_OUT_MIN = 0.0;      // Pressure calibration lower point
double CST_PRESSURE_OUT_MAX = 200.0;    // Pressure calibration upper point. This is in mmHg. This is about the max it can do.
double CST_CAL_PRESSURE_MIN = 0.0;      // As with before, in mmHg.
double CST_CAL_PRESSURE_MAX = 200.0;    // As with before, in mmHg.
// int    CST_PRESSURE_IN_MIN2 = 100;      // Raw value calibration lower point
// int    CST_PRESSURE_IN_MAX2 = 400;      // Raw value calibration upper point
// double CST_PRESSURE_OUT_MIN2 = 0.0;     // Pressure calibration lower point
// double CST_PRESSURE_OUT_MAX2 = 200.0;   // Pressure calibration upper point. This is in mmHg. This is about the max it can do.
// double CST_CAL_PRESSURE_MIN2 = 0.0;     // As with before, in mmHg.
// double CST_CAL_PRESSURE_MAX2 = 200.0;   // As with before, in mmHg.
const int CST_CAL_STEP_SM = 1;          // Change this to change what the L/R buttons do during calibration.
const int CST_CAL_STEP_LG = 10;         // Change this to change what the U/D buttons do during calibration.
int choice;

//  Setup the data recording (data to be sent out, sampling rate)
//******************************************************************************************************************
  #define       NUMSAMPLES 50               //  Change this to alter the number of samples averaged.                *
  unsigned long TIME_DELAY = 100;           //  Change this to alter the time delay for wheatstone bridge output.   *
  unsigned long LCD_TIME_DELAY = 500;           // Setting a delay to update the LCD screen
//******************************************************************************************************************

double samples1[NUMSAMPLES];      // Needed to determine how the samples will be summed and averaged.
double samples2[NUMSAMPLES];      // Needed to determine how the samples will be summed and averaged.
unsigned long previousMillis = 0;        // Resetting the clock to determine how much time has elapsed.
unsigned long initMillis = 0;            // Resetting the clock to determine how much time has elapsed.
unsigned long elapsedMillis = 0;
unsigned long currentMillis_LCD = millis();
bool update_flag = 0;                    // Flag to update the LCD display

//  Initialize the Wheatstone bridge object, plugged into Strain2 on the shield
WheatstoneBridge wsb1(A1, CST_PRESSURE_IN_MIN, CST_PRESSURE_IN_MAX, CST_PRESSURE_OUT_MIN, CST_PRESSURE_OUT_MAX);

//  Initialize the Wheatstone bridge object, plugged into Strain2 on the shield
WheatstoneBridge wsb2(A0, CST_PRESSURE_IN_MIN, CST_PRESSURE_IN_MAX, CST_PRESSURE_OUT_MIN, CST_PRESSURE_OUT_MAX);

//  All Setup functions go in here: calibrate transducer, regulate everything, etc.
void setup()
{
  //  Transducer 1: Calibration and variables needed for linear interpolation
  int cal_adc_low = CST_PRESSURE_IN_MIN;
  int cal_adc_high = CST_PRESSURE_IN_MAX;
  int cal_pressure_low = CST_PRESSURE_OUT_MIN;
  int cal_pressure_high = CST_PRESSURE_OUT_MAX;
    //  Transducer 2: Calibration and variables needed for linear interpolation
  int cal_adc_low2 = CST_PRESSURE_IN_MIN;
  int cal_adc_high2 = CST_PRESSURE_IN_MAX;
  int cal_pressure_low2 = CST_PRESSURE_OUT_MIN;
  int cal_pressure_high2 = CST_PRESSURE_OUT_MAX;
  
  //  Initialize LCD screen and intro
  lcd.begin(16, 2); displayScreen("VasoTracker", "Pressure Monitor"); delay(3000);

  choice = startup("Recalibrate?  NO", "Select (UP/DOWN)", "YES", " NO", 13);

  if(choice == 1) {
    //Calibrate the first pressure transducer!
    displayScreen("* Calibration *", "Transducer 1"); delay(1000);
  
    // Calibration 1: low value. Get low pressure value and associated ADC value.
    displayScreen("* Calibration *", "Low value"); delay(1000);
    cal_adc_low     = getValueADC("Set low raw ADC", "Raw ADC:", 13, A1, btnSELECT);
    cal_pressure_low   = getValueInRange("Set low pressure", "Pres (mmHg):", 13, cal_pressure_low, CST_CAL_PRESSURE_MIN, CST_CAL_PRESSURE_MAX, CST_CAL_STEP_SM, CST_CAL_STEP_LG);
  
    // Calibration 1: high value. Get high pressure value and associated ADC value.
    displayScreen("* Calibration *", "High value"); delay(1000);
    cal_adc_high    = getValueADC("Set high raw ADC", "Raw ADC:", 13, A1, btnSELECT);
    cal_pressure_high  = getValueInRange("Set high pressure", "Pres (mmHg):", 13, cal_pressure_high, CST_CAL_PRESSURE_MIN, CST_CAL_PRESSURE_MAX, CST_CAL_STEP_SM, CST_CAL_STEP_LG);

// Calibration 2: Low value. Get low pressure value and associated ADC value.
  displayScreen("* Calibration *", "Low value"); delay(1000);
  cal_adc_low2     = getValueADC("Set low raw ADC", "Raw ADC:", 13, A0, btnSELECT);
  cal_pressure_low2   = getValueInRange("Set low pressure", "Pres (mmHg):", 13, cal_pressure_low2, CST_CAL_PRESSURE_MIN, CST_CAL_PRESSURE_MAX, CST_CAL_STEP_SM, CST_CAL_STEP_LG);

  // Calibration 2: high value. Get high pressure value and associated ADC value.
  displayScreen("* Calibration *", "High value"); delay(1000);
  cal_adc_high2 = getValueADC("Set high raw ADC", "Raw ADC:", 13, A0, btnSELECT);
  cal_pressure_high2 = getValueInRange("Set high pressure", "Pres (mmHg):", 13, cal_pressure_high2, CST_CAL_PRESSURE_MIN, CST_CAL_PRESSURE_MAX, CST_CAL_STEP_SM, CST_CAL_STEP_LG);

    //Save calibration values]
    
    writeIntIntoEEPROM(16, cal_adc_low);
    writeIntIntoEEPROM(20, cal_pressure_low);
    writeIntIntoEEPROM(24, cal_adc_high);
    writeIntIntoEEPROM(28, cal_pressure_high);
    writeIntIntoEEPROM(32, cal_adc_low2);
    writeIntIntoEEPROM(36, cal_pressure_low2);
    writeIntIntoEEPROM(40, cal_adc_high2);
    writeIntIntoEEPROM(44, cal_pressure_high2);
    displayScreen("* Please Wait *", "Saving Settings");
    delay(2000);
    lcd.begin(16, 2);
     }
  else if(choice == 0){
    displayScreen("* Please Wait *", "Loading Settings");
    cal_adc_low = readIntFromEEPROM(16); 
    cal_pressure_low = readIntFromEEPROM(20);
    cal_adc_high = readIntFromEEPROM(24);
    cal_pressure_high = readIntFromEEPROM(28);
    cal_adc_low2 = readIntFromEEPROM(32); 
    cal_pressure_low2 = readIntFromEEPROM(36);
    cal_adc_high2 = readIntFromEEPROM(40);
    cal_pressure_high2 = readIntFromEEPROM(44);
    delay(2000);
    lcd.begin(16, 2);
  }
  //  Perform linear calibration based on values chosen and selected above for transducer 1.
  wsb1.linearCalibration(cal_adc_low, cal_adc_high, cal_pressure_low, cal_pressure_high);
  wsb2.linearCalibration(cal_adc_low2, cal_adc_high2, cal_pressure_low2, cal_pressure_high2);
  
  //  Initialize serial communication and set display labels.
  // Setup display labels
  Serial.begin(9600);
  lcd.begin(16,2);
  displayScreen("P1 (mmHg):", "P2 (mmHg):");
}
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
